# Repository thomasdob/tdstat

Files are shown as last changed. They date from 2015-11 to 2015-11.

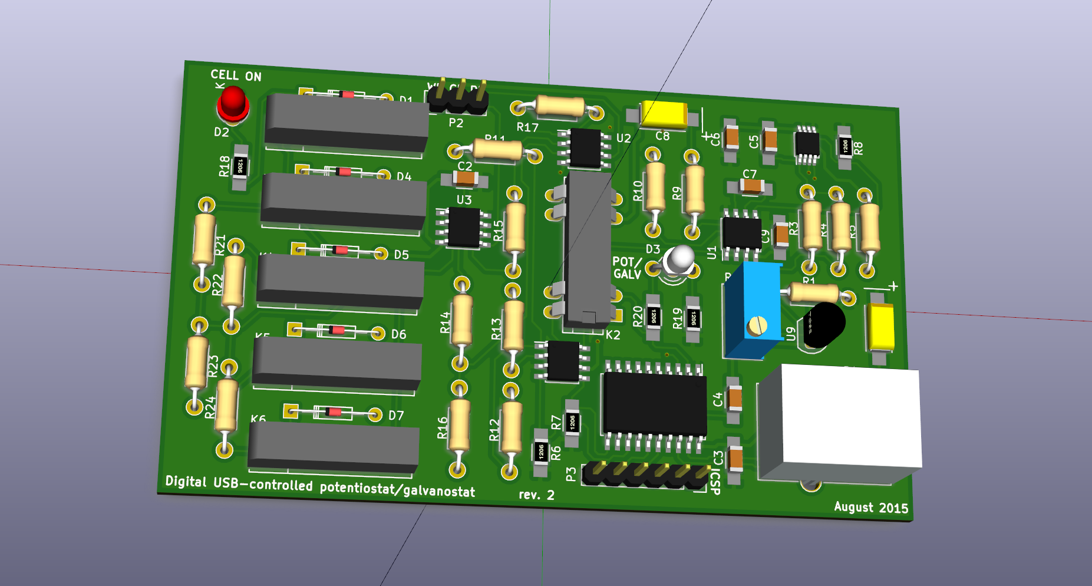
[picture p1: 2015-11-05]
3d_render.png

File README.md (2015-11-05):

# tdstat
An open source USB-controlled potentiostat/galvanostat.

I started this project because I needed a potentiostat/galvanostat that suited my research on thin-film lithium-ion batteries. Commercial offers exist, but even a basic model will easily set you back €6000. Moreover, I didn't like dealing with closed, non-user-serviceable hardware and putting up with the manufacturer's buggy software. So I designed and built my own, for a parts cost of about €50.

This repository contains everything necessary to replicate the design. It consists of a circuit schematic and PCB layout made with KiCad, microcontroller firmware and source code written in C, and a demonstration program written in LabVIEW to run typical electrochemical measurements.

More information can be found on the Wiki.

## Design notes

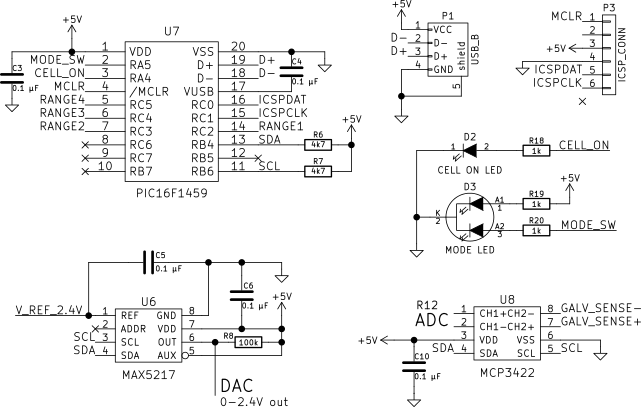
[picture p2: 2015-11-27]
docs/schematic_part4.png

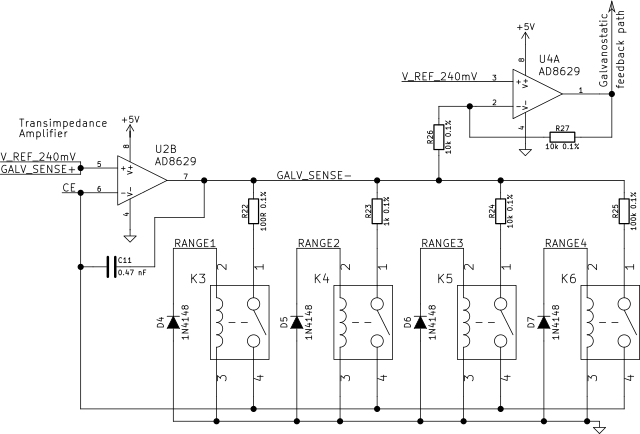
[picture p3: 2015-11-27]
docs/schematic_part3.png

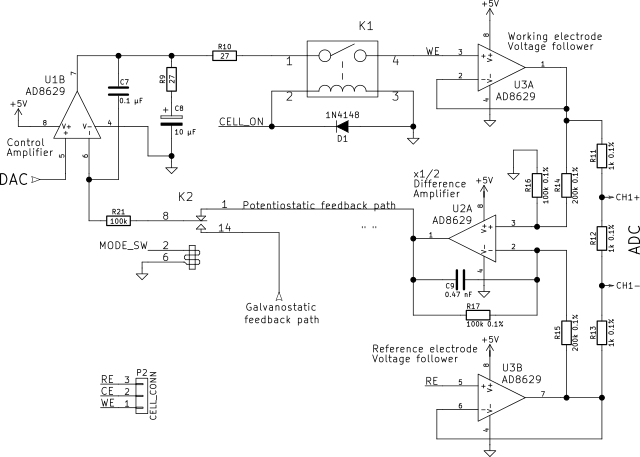
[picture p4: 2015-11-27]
docs/schematic_part2.png

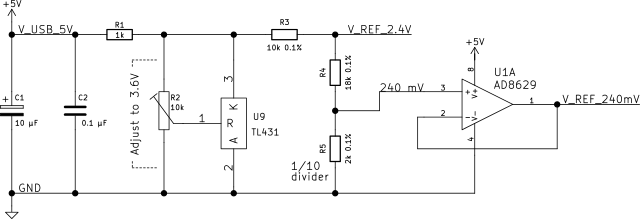
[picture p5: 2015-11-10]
docs/schematic_part1.png

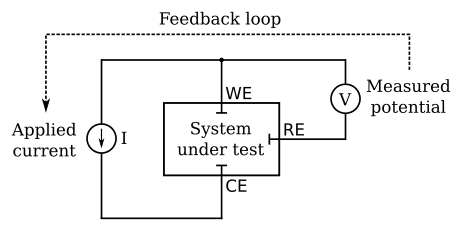
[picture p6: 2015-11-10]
docs/basic_potentiostat_diagram.png

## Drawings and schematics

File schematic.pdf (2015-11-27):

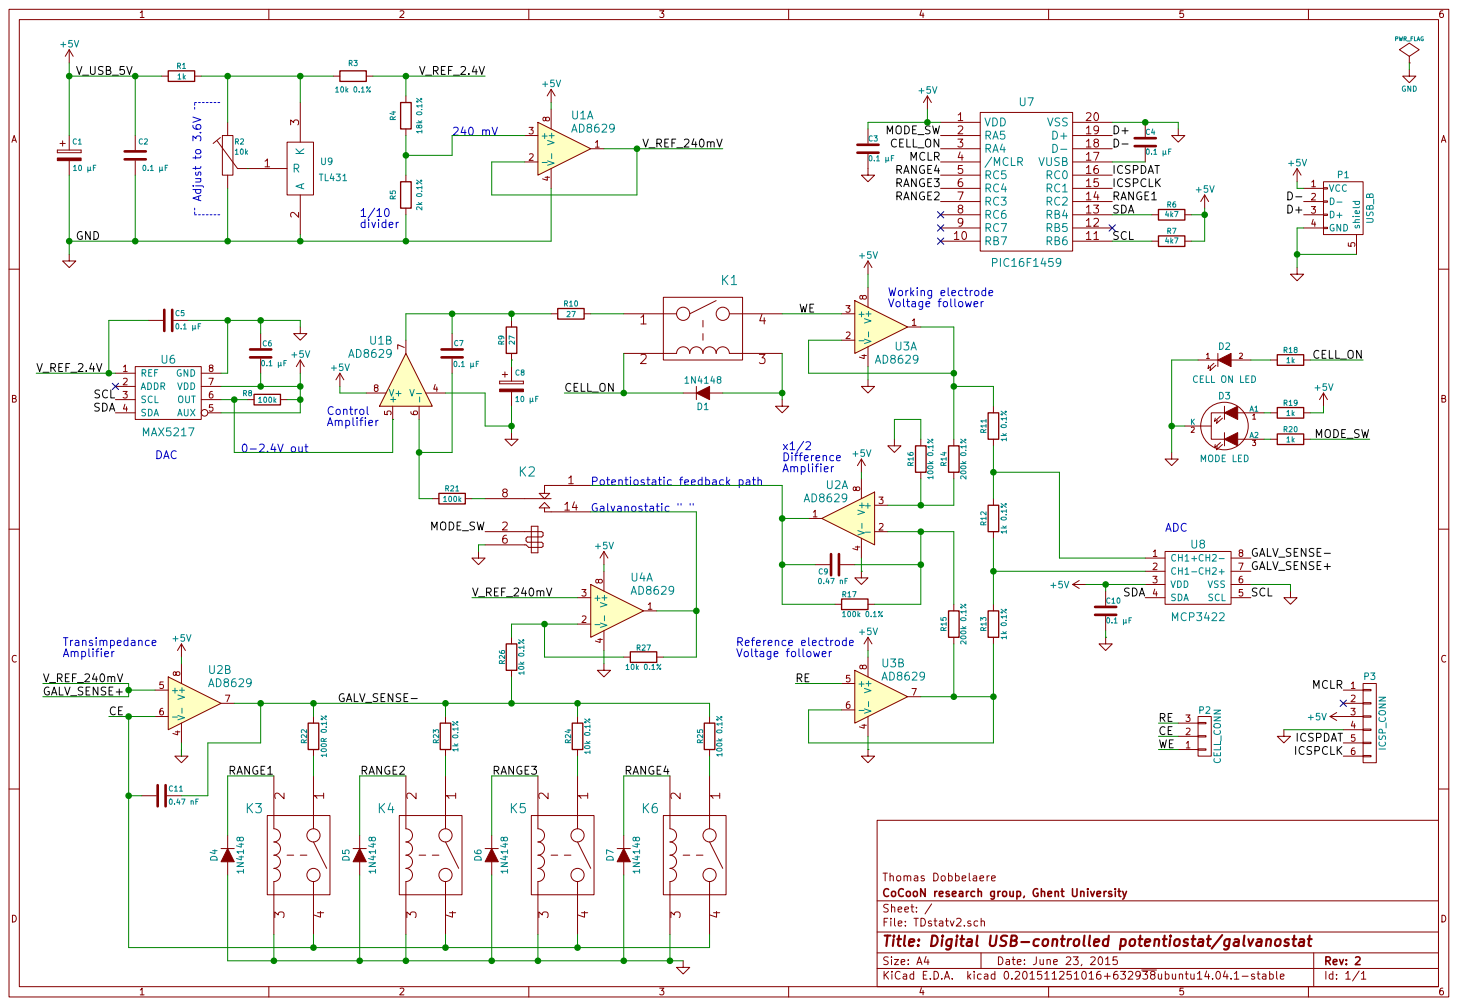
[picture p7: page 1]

Voltage follower Reference electrode Voltage follower

Id: 1/1 Title: Digital USB-controlled potentiostat/galvanostat File: TDstatv2.sch Sheet: / CoCooN research group, Ghent University Thomas Dobbelaere

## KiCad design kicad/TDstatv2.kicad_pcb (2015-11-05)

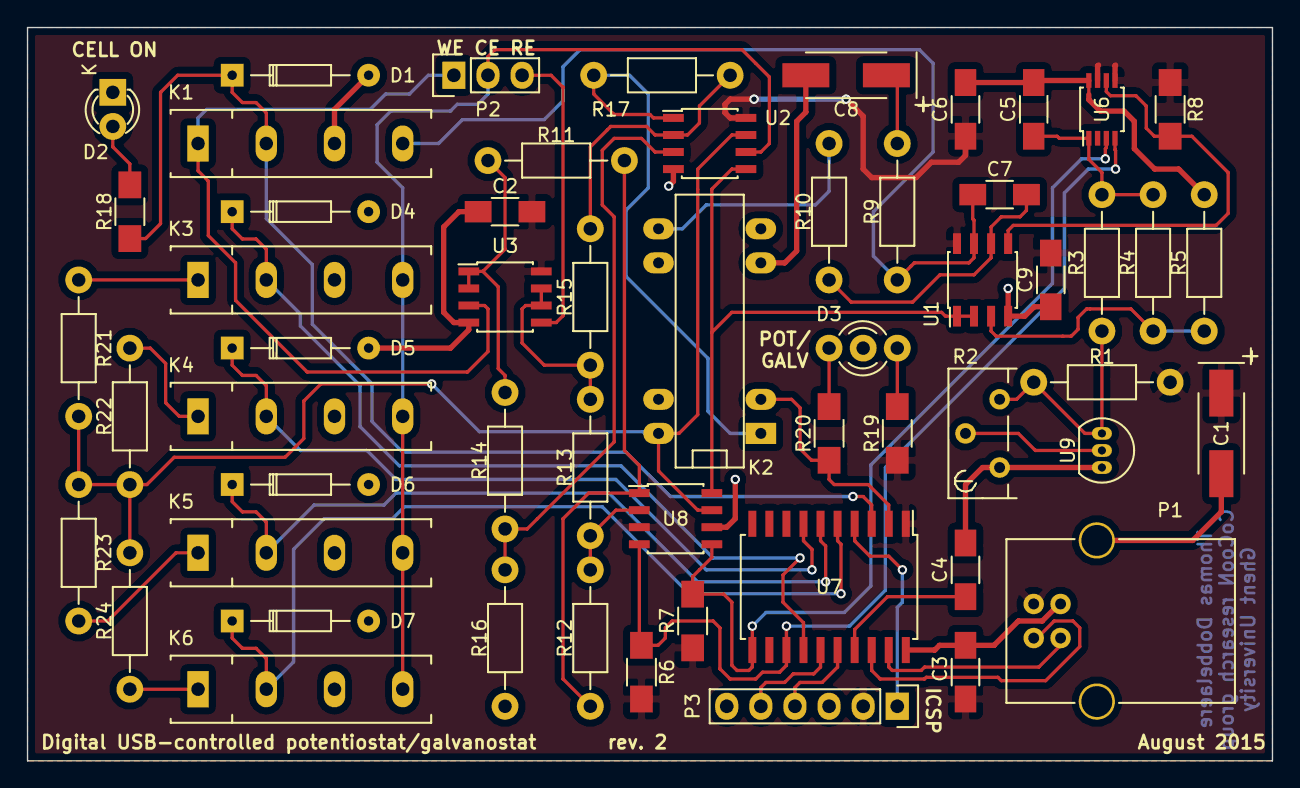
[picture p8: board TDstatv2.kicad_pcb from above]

Board: 2 copper layers, 92.7 x 54.6 mm, 56 parts (0 on the bottom side), 44 nets.

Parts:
C1, C8: 10 µF; TantalC_SizeC_EIA-6032_HandSoldering
C2, C3, C4, C5, C6, C7, C9: 0.1 µF; C_1206_HandSoldering
D1, D4, D5, D6, D7: 1N4148; Diode_DO-35_SOD27_Horizontal_RM10
D2: CELL ON LED; LED-3MM
D3: MODE LED; DUO-LED-3mm
K1, K3, K4, K5, K6: 9007-05-00; RELAY-9007
K2: HE721C0510; RELAY-HE700
P1: USB_B
P2: CELL_CONN; Pin_Header_Straight_1x03
P3: ICSP_CONN; Pin_Header_Straight_1x06
R1: 1k; Resistor_Horizontal_RM10mm
R2: 10k; Potentiometer_Bourns_3296Y_3-8Zoll_Angular_ScrewUp
R3, R23: 10k 0.1%; Resistor_Horizontal_RM10mm
R4: 18k 0.1%; Resistor_Horizontal_RM10mm
R5: 2k 0.1%; Resistor_Horizontal_RM10mm
R6, R7: 4k7; R_1206_HandSoldering
R8: 100k; R_1206_HandSoldering
R9: 27; Resistor_Horizontal_RM10mm
R10: 100k; Resistor_Horizontal_RM10mm
R11, R12, R13, R22: 1k 0.1%; Resistor_Horizontal_RM10mm
R14, R15: 200k 0.1%; Resistor_Horizontal_RM10mm
R16, R17, R24: 100k 0.1%; Resistor_Horizontal_RM10mm
R18, R19, R20: 1k; R_1206_HandSoldering
R21: 100R 0.1%; Resistor_Horizontal_RM10mm
U1, U2, U3: AD8629; SOIC-8_3.9x4.9mm_Pitch1.27mm
U6: MAX5217; TSSOP-8_3x3mm_Pitch0.65mm
U7: PIC16F1459; SOIC-20_7.5x12.8mm_Pitch1.27mm
U8: MCP3422; SOIC-8_3.9x4.9mm_Pitch1.27mm
U9: TL431; TO-92_Inline_Narrow_Oval

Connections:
+5V: C1.1, C2.1, C3.1, C6.1, C9.1, P1.1, P3.2, R1.2, R6.1, R7.1, R8.2, R19.2, U1.8, U2.8, U3.8, U6.5, U6.7, U7.1, U8.3
/CE: K3.4, K4.4, K5.4, K6.4, P2.2, U2.6
/CELL_ON: D1.1, K1.2, R18.2, U7.3
/D+: P1.3, U7.19
/D-: P1.2, U7.18
/GALV_SENSE+: U1.1, U1.2, U2.5, U8.8
/GALV_SENSE-: K2.14, R21.2, R22.2, R23.2, R24.2, U2.7, U8.7
/ICSPCLK: P3.5, U7.15
/ICSPDAT: P3.4, U7.16
/MCLR: P3.1, U7.4
/MODE_SW: K2.2, R20.2, U7.2
/RANGE1: D4.1, K3.2, U7.14
/RANGE2: D5.1, K4.2, U7.7
/RANGE3: D6.1, K5.2, U7.6
/RANGE4: D7.1, K6.2, U7.5
/RE: P2.3, U3.5
/SCL: R7.2, U6.3, U7.11, U8.5
/SDA: R6.2, U6.4, U7.13, U8.4
/V_REF_2.4V: C5.2, R3.2, R4.2, U6.1
/WE: K1.1, P2.1, U3.3
GND: C1.2, C2.2, C3.2, C4.1, C5.1, C6.2, C8.2, C9.2, D1.2, D2.1, D3.2, D4.2, D5.2, D6.2, D7.2, K1.3, K2.6, K3.3, K4.3, K5.3, K6.3, P1.4, P1.5, P3.3, R2.1, R5.1, R16.2, U1.4, U2.4, U3.4, U6.8, U7.20, U8.6, U9.3
unnamed: C4.2, U7.17
unnamed: C7.1, K1.4, R9.1, U1.7
unnamed: C7.2, R10.2, U1.6
unnamed: C8.1, R9.2
unnamed: D2.2, R18.1
unnamed: D3.1, R19.1
unnamed: D3.3, R20.1
unnamed: K2.1, R17.2, U2.1
unnamed: K2.8, R10.1
unnamed: K3.1, R21.1
unnamed: K4.1, R22.1
unnamed: K5.1, R23.1
unnamed: K6.1, R24.1
unnamed: R1.1, R2.3, R3.1, U9.1
unnamed: R2.2, U9.2
unnamed: R4.1, R5.2, U1.3
unnamed: R8.1, U1.5, U6.6
unnamed: R11.1, R12.2, U8.1
unnamed: R11.2, R14.2, U3.1, U3.2
unnamed: R12.1, R13.2, U8.2
unnamed: R13.1, R15.1, U3.6, U3.7
unnamed: R14.1, R16.1, U2.3
unnamed: R15.2, R17.1, U2.2

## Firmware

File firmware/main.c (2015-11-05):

/*
 * USB Potentiostat/galvanostat firmware
 *
 * This code makes use of Signal 11's M-Stack USB stack to implement 
 * communication through raw USB bulk transfers. Commands are received
 * as ASCII strings on EP1 OUT. They are then interpreted and executed;
 * they either change the state of output pins, or cause data to be read
 * from / written to the MCP3422 (ADC) or MAX5217 (DAC) using a software
 * I2C implementation (hardware I2C was tested but did not work properly).
 * The resulting data, or an "OK" message, is sent as a reply on EP1 IN.
 * The USB service is interrupt-driven.
 *
 * Thomas Dobbelaere
 * CoCooN research group
 * 2015-08-27
 */

#include "usb.h"
#include <xc.h>
#include <string.h>
#include "usb_config.h"
#include "usb_ch9.h"
#include "i2c_software.h"

// PIC16F1459 configuration bit settings:
// CONFIG1
#pragma config FOSC = INTOSC    // Oscillator Selection Bits (INTOSC oscillator: I/O function on CLKIN pin)
#pragma config WDTE = OFF       // Watchdog Timer Enable (WDT disabled)
#pragma config PWRTE = OFF      // Power-up Timer Enable (PWRT disabled)
#pragma config MCLRE = OFF      // MCLR Pin Function Select (MCLR/VPP pin function is digital input)
#pragma config CP = OFF         // Flash Program Memory Code Protection (Program memory code protection is disabled)
#pragma config BOREN = ON       // Brown-out Reset Enable (Brown-out Reset enabled)
#pragma config CLKOUTEN = OFF   // Clock Out Enable (CLKOUT function is disabled. I/O or oscillator function on the CLKOUT pin)
#pragma config IESO = OFF       // Internal/External Switchover Mode (Internal/External Switchover Mode is disabled)
#pragma config FCMEN = OFF      // Fail-Safe Clock Monitor Enable (Fail-Safe Clock Monitor is disabled)

// CONFIG2
#pragma config WRT = OFF        // Flash Memory Self-Write Protection (Write protection off)
#pragma config CPUDIV = NOCLKDIV// CPU System Clock Selection Bit (NO CPU system divide)
#pragma config USBLSCLK = 48MHz // USB Low SPeed Clock Selection bit (System clock expects 48 MHz, FS/LS USB CLKENs divide-by is set to 8.)
#pragma config PLLMULT = 3x     // PLL Multipler Selection Bit (3x Output Frequency Selected)
#pragma config PLLEN = ENABLED  // PLL Enable Bit (3x or 4x PLL Enabled)
#pragma config STVREN = ON      // Stack Overflow/Underflow Reset Enable (Stack Overflow or Underflow will cause a Reset)
#pragma config BORV = LO        // Brown-out Reset Voltage Selection (Brown-out Reset Voltage (Vbor), low trip point selected.)
#pragma config LPBOR = OFF      // Low-Power Brown Out Reset (Low-Power BOR is disabled)
#pragma config LVP = OFF        // Low-Voltage Programming Enable (High-voltage on MCLR/VPP must be used for programming)

#define MODE_SW LATAbits.LATA5
#define MODE_SW_TRIS TRISAbits.TRISA5
#define CELL_ON_PIN LATAbits.LATA4
#define CELL_ON_TRIS TRISAbits.TRISA4
#define CELL_ON  1
#define CELL_OFF 0
#define POTENTIOSTATIC  0
#define GALVANOSTATIC  1
#define PIN_INPUT  1
#define PIN_OUTPUT 0
#define RANGE1 0x04 // RC2 high, everything else low
#define RANGE2 0x08 // RC3 high, everything else low
#define RANGE3 0x10 // RC4 high, everything else low
#define RANGE4 0x20 // RC5 high, everything else low

static const uint8_t* received_data;
static uint8_t received_data_length;
static uint8_t* transmit_data;
static uint8_t transmit_data_length;

void MAX5217_load_code(uint8_t value_hi, uint8_t value_lo)
{
	StartI2C();
	WriteI2C(0x3A); // I2C address (for writing)
	WriteI2C(0x01); // CODE_LOAD command
	WriteI2C(value_hi); // DAC value <15:8>
	WriteI2C(value_lo); // DAC value <7:0>
	StopI2C();
}

void MCP3422_config(uint8_t config_byte)
{
	StartI2C();
	WriteI2C(0xD0); // I2C address (for writing)
	WriteI2C(config_byte); // CODE_LOAD command
	StopI2C();
}

void MCP3422_read3(uint8_t* byte1, uint8_t* byte2, uint8_t* config_byte)
{
	StartI2C();
	WriteI2C(0xD1); // I2C address (for reading)
	*byte1 = ReadI2C();
	*byte2 = ReadI2C();
	*config_byte = ReadLastI2C();
	StopI2C();
}

void MCP3422_read4(uint8_t* byte1, uint8_t* byte2, uint8_t* byte3, uint8_t* config_byte)
{
	StartI2C();
	WriteI2C(0xD1); // I2C address (for reading)
	*byte1 = ReadI2C();
	*byte2 = ReadI2C();
	*byte3 = ReadI2C();
	*config_byte = ReadLastI2C();
	StopI2C();
}

void command_unknown()
{
	const uint8_t* reply = "?";
    strcpy(transmit_data, reply);
    transmit_data_length = strlen(reply);
}

void send_OK()
{
	const uint8_t* reply = "OK";
    strcpy(transmit_data, reply);
    transmit_data_length = strlen(reply);
}

void command_cell_on()
{
	CELL_ON_PIN = CELL_ON;
	send_OK();
}

void command_cell_off()
{
	CELL_ON_PIN = CELL_OFF;
	send_OK();
}

void command_mode_potentiostatic()
{
	MODE_SW = POTENTIOSTATIC;
	send_OK();
}

void command_mode_galvanostatic()
{
	MODE_SW = GALVANOSTATIC;
	send_OK();
}

void command_range1()
{
	LATC = RANGE1;
	send_OK();
}

void command_range2()
{
	LATC = RANGE2;
	send_OK();
}

void command_range3()
{
	LATC = RANGE3;
	send_OK();
}

void command_range4()
{
	LATC = RANGE4;
	send_OK();
}

void command_set_dac(uint8_t value_hi, uint8_t value_lo)
{
	MAX5217_load_code(value_hi, value_lo);
	send_OK();
}

void command_config_adc(uint8_t config_byte)
{
	MCP3422_config(config_byte);
	send_OK();
}

void command_read_adc_3bytes()
{
	uint8_t byte1, byte2, config_byte;
	MCP3422_read3(&byte1, &byte2, &config_byte);
	transmit_data[0]=byte1;
	transmit_data[1]=byte2;
	transmit_data[2]=config_byte;
	transmit_data_length=3;
}

void command_read_adc_4bytes()
{
	uint8_t byte1, byte2, byte3, config_byte;
	MCP3422_read4(&byte1, &byte2, &byte3, &config_byte);
	transmit_data[0]=byte1;
	transmit_data[1]=byte2;
	transmit_data[2]=byte3;
	transmit_data[3]=config_byte;
	transmit_data_length=4;
}

void interpret_command() {
    if (received_data_length == 7 && strncmp(received_data,"CELL ON",7) == 0)
        command_cell_on();
    else if (received_data_length == 8 && strncmp(received_data,"CELL OFF",8) == 0)
        command_cell_off();
    else if (received_data_length == 14 && strncmp(received_data,"POTENTIOSTATIC",14) == 0)
        command_mode_potentiostatic();
    else if (received_data_length == 13 && strncmp(received_data,"GALVANOSTATIC",13) == 0)
        command_mode_galvanostatic();
    else if (received_data_length == 7 && strncmp(received_data,"RANGE 1",7) == 0)
        command_range1();
	else if (received_data_length == 7 && strncmp(received_data,"RANGE 2",7) == 0)
        command_range2();
	else if (received_data_length == 7 && strncmp(received_data,"RANGE 3",7) == 0)
        command_range3();
	else if (received_data_length == 7 && strncmp(received_data,"RANGE 4",7) == 0)
        command_range4();
	else if (received_data_length == 9 && strncmp(received_data,"DACSET ",7) == 0)
		command_set_dac(received_data[7],received_data[8]);
	else if (received_data_length == 9 && strncmp(received_data,"ADCCONF ",8) == 0)
		command_config_adc(received_data[8]);
	else if (received_data_length == 8 && strncmp(received_data,"ADCREAD3",8) == 0)
		command_read_adc_3bytes();
	else if (received_data_length == 8 && strncmp(received_data,"ADCREAD4",8) == 0)
		command_read_adc_4bytes();
	else
        command_unknown();
}

int main(void)
{
	OSCCONbits.IRCF = 0b1111; // 0b1111 = 16MHz HFINTOSC postscaler
    ANSELA = 0x00; // digital I/O on PORTA
    ANSELB = 0x00; // digital I/O on PORTB
    ANSELC = 0x00; // digital I/O on PORTC
    APFCON = 0x00; // a little bit of voodoo
    MODE_SW_TRIS = PIN_OUTPUT;
    MODE_SW = POTENTIOSTATIC; // initialize mode to potentiostatic
    CELL_ON_TRIS = PIN_OUTPUT;
    CELL_ON_PIN = CELL_OFF; // initialize cell to off position
    TRISC = 0x00; // all outputs on PORTC
    LATC = RANGE1; // initialize range to range 1

	// Enable Active clock-tuning from the USB
	ACTCONbits.ACTSRC = 1; // 1=USB
	ACTCONbits.ACTEN = 1;

	// Configure interrupts
	INTCONbits.PEIE = 1;
	INTCONbits.GIE = 1;
	
	// Initialize USB
	usb_init();

	while (1)
	{
		if (usb_is_configured() && usb_out_endpoint_has_data(1)) // wait for data received from host
		{
			if (!usb_in_endpoint_halted(1))
			{
				while (usb_in_endpoint_busy(1)) // wait for EP1 IN to become free
					;
				received_data_length = usb_get_out_buffer(1, &received_data);
				transmit_data = usb_get_in_buffer(1);
				interpret_command(); // this reads received_data and sets transmit_data and transmit_data_length
				usb_send_in_buffer(1, transmit_data_length); // send the data back
			}
			usb_arm_out_endpoint(1);
		}
	}

	return 0;
}

void interrupt isr()
{
	usb_service();
}

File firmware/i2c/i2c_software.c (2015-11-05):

#include "i2c_software.h"

void StartI2C()
{
  CLOCK_HI;                    // release clock pin to float high
  DATA_LAT = 0;                // set data pin latch to 0
  DATA_LOW;                    // set pin to output to drive low
  _delay(100);
}

void StopI2C()
{
  SCLK_LAT = 0;                // set clock pin latch to 0
  CLOCK_LOW;                   // set clock pin to output to drive low
  DATA_LAT = 0;                // set data pin latch to 0
  DATA_LOW;                    // set data pin output to drive low
  _delay(100);                 // user may need to modify based on Fosc
  CLOCK_HI;                    // release clock pin to float high
  _delay(100);                 // user may need to modify based on Fosc
  DATA_HI;                     // release data pin to float high
  _delay(100);                 // user may need to modify based on Fosc
}

uint8_t ReadI2C()
{
  uint8_t I2C_BUFFER = 0;      // data to be read in
  uint8_t BIT_COUNTER = 8;     // set bit count for byte 
  SCLK_LAT = 0;                // set clock pin latch to 0
  DATA_HI;                     // release data line to float high
  do
  {
    CLOCK_LOW;                 // set clock pin output to drive low
    _delay(100);               // user may need to modify based on Fosc
    CLOCK_HI;                  // release clock line to float high
    _delay(100);               // user may need to modify based on Fosc

    I2C_BUFFER <<= 1;          // shift composed byte by 1
    I2C_BUFFER &= 0xFE;        // clear bit 0

    if ( DATA_PIN )            // is data line high
     I2C_BUFFER |= 0x01;       // set bit 0 to logic 1
   
  } while ( --BIT_COUNTER );   // stay until 8 bits have been acquired
  CLOCK_LOW;                   //------------------*
  DATA_LAT = 0;                //                  *
  DATA_LOW;                    //   Generate Ack   *
  _delay(100);                 //                  *
  CLOCK_HI;                    //                  *
  _delay(100);                 //------------------*
  return I2C_BUFFER ;          // return with data
}

uint8_t ReadLastI2C()
{
  uint8_t I2C_BUFFER = 0;      // data to be read in
  uint8_t BIT_COUNTER = 8;     // set bit count for byte 
  SCLK_LAT = 0;                // set clock pin latch to 0
  DATA_HI;                     // release data line to float high
  do
  {
    CLOCK_LOW;                 // set clock pin output to drive low
    _delay(100);               // user may need to modify based on Fosc
    CLOCK_HI;                  // release clock line to float high
    _delay(100);               // user may need to modify based on Fosc

    I2C_BUFFER <<= 1;          // shift composed byte by 1
    I2C_BUFFER &= 0xFE;        // clear bit 0

    if ( DATA_PIN )            // is data line high
     I2C_BUFFER |= 0x01;       // set bit 0 to logic 1
   
  } while ( --BIT_COUNTER );   // stay until 8 bits have been acquired
  CLOCK_LOW;                   //------------------*
  _delay(100);                 //   Generate Nack  *
  CLOCK_HI;                    //                  *
  _delay(100);                 //------------------*
  return I2C_BUFFER ;          // return with data
}

void WriteI2C(uint8_t data_out)
{
  uint8_t BIT_COUNTER = 8;        // initialize bit counter
  uint8_t I2C_BUFFER = data_out;  // data to be sent out
  SCLK_LAT = 0;                   // set clock pin latch to 0
  do
  {
	  CLOCK_LOW;                  // set clock pin output to drive low
	  if ( I2C_BUFFER & 0x80 )    // if MSB set, transmit out logic 1
	  {
		DATA_HI;                  // release data line to float high 
	  }
	  else                        // transmit out logic 0
	  {
		DATA_LAT = 0;             // set data pin latch to 0
		DATA_LOW;                 // set data pin output to drive low 
	  }
	  _delay(100);              // user may need to modify based on Fosc
	  CLOCK_HI;                 // release clock line to float high 
	  _delay(100);              // user may need to modify based on Fosc

	  I2C_BUFFER <<= 1;
	  BIT_COUNTER --;           // reduce bit counter by 1
  } while (BIT_COUNTER);        // stay in transmit loop until byte sent
  CLOCK_LOW;                      // 
  _delay(100);                    //
  CLOCK_HI;                       // waits for Ack from device
  _delay(100);                    //
}

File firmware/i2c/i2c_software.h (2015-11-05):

#ifndef __SWI2C16_H
#define __SWI2C16_H

#include <stdint.h>
#include <stdbool.h>
#include <stdlib.h>
#include <xc.h>

#define  DATA_LOW   TRISBbits.TRISB4 = 0; // define macro for data pin output
#define  DATA_HI    TRISBbits.TRISB4 = 1; // define macro for data pin input
#define  DATA_LAT   LATBbits.LATB4        // define macro for data pin latch
#define  DATA_PIN   PORTBbits.RB4         // define macro for data pin

#define  CLOCK_LOW  TRISBbits.TRISB6 = 0; // define macro for clock pin output
#define  CLOCK_HI   TRISBbits.TRISB6 = 1; // define macro for clock pin input
#define  SCLK_LAT   LATBbits.LATB6        // define macro for clock pin latch
#define  SCLK_PIN   PORTBbits.RB6         // define macro for clock pin

void StartI2C();
void StopI2C();
uint8_t ReadI2C();
uint8_t ReadLastI2C();
void WriteI2C(uint8_t data_out);

#endif
